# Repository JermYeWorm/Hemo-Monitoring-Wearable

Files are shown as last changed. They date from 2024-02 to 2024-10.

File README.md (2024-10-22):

# Hemodynamic Health Monitoring Wearable Platform
This device is an open-source, programmable, highly-integrated wearable platform capable of simultaneously measuring multiple hemodynamic biosignals. The goal is to enable real time processing by integrating both analog front end and edge ML, before wireless transmit. Our most recent paper can be found [here](https://doi.org/10.1109/MWSCAS60917.2024.10658959).
<br><br>
The current revision is electrical bioimpedance (EBI), electrocardiogram (ECG), and photoplethysmography (PPG) bio-monitoring enabled, and contains an onboard microprocessor and BLE transmit module.
<br><br>
The ongoing work on this project is with the Shah lab at the University of Maryland, College Park.
<br><br>

<br><br>

## System Flowchart

<br><br>

## Hardware
All PCB schematic capture and board layout was done with Altium Designer 2024.

The wearable platform runs on a BLE capable nRF52840 MCU SoC within a NINA-B302 FIFA antenna module. 
<br><br>
The MCU pinout is chosen to match the I2C, SPI, and spare analog/digital pins of an Arduino Nano 33 BLE. This allows for programmming via Arduino IDE after the burning of an Arduino Nano 33 BLE bootloader without the need for internal Arduino library pinout modifications. The MCU may also be programmed directly using the nRF Connect SDK.
<br><br>
The MCU is an open CPU and will require access through the SWD interface to enable programming through the USB port. A standard JLink with a 10 pin SWD cable connected to the J1 connector will allow for hardware debug and burning of bootloaders. 
<br><br>

<br>

<br><br>

### Schematic
Hierarchical Schematic Structure:<br>
```
├── [1] ipg_wearable.SchDoc
        ├── [2] sensors.SchDoc
        ├── [3] connectors.SchDoc
        └── [4] power_supply.SchDoc
```
<br>

1714973704757-3ba7de04-8b89-4758-92bf-7abcabce8b58_1
<br>

1714973704757-3ba7de04-8b89-4758-92bf-7abcabce8b58_2
<br>

1714973704757-3ba7de04-8b89-4758-92bf-7abcabce8b58_3
<br>

1714973704757-3ba7de04-8b89-4758-92bf-7abcabce8b58_4
<br><br>

### Board Layout

<br>_Fig 1. Top Layer (Signal)_<br><br>

<br>_Fig 2. GND Layer_<br><br>

<br>_Fig 3. PWR Layer_<br><br>

<br>_Fig 4. Bottom Layer (Signal)_<br><br>

<br>_Fig 5. Mechanical + Dimensions_<br><br>

### Fabricated Device

<br>_Fig 1. Front View_<br><br>


<br>_Fig 2. Back View (PPG Components Visible)_<br><br>

## Results

<br>_**(Top)** ECG with real time R-to-R detection using the onboard biopotential front end. **(Bottom)** EBI demonstration with electrodes placed across the thoracic cavity during respiration._<br><br>

## Contact
Inquiry about this repository can be directed towards jyun1129@umd.edu.

## Contributors
Primary Developer - Jeremy Yun (jyun1129@umd.edu)
<br>
Principal Investigator - Dr. Sahil Shah (sshah389@umd.edu)
<br>

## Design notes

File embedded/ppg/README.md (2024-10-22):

# PPG Front End Firmware

This directory contains jumpstarter resources for MAXM86146 firmware development. The MAXM86146 is pre-flashed with a programmable bootloader, and requires manual programming of an .msbl hex file via I2C to access application mode.
<br><br>
An .msbl flashing application can be found in "MAX32630FTHR_msbl_flasher" (requires external MAX32630FTHR board and 3.3V to 1.8V level shifter). 
<br><br>
"MAX32664C_33.13.31_MAXM86146.zip" contains the latest documentation from Maxim Integrated on the internal MAX32664C MCU.

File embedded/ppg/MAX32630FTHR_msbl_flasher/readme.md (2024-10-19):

# About
Software and firmware for flashing .msbl files using the [MAX32630FTHR](https://www.maximintegrated.com/en/products/microcontrollers/MAX32630FTHR.html).  This software flashes .msbl files onto a [MAX32664](https://www.maximintegrated.com/en/products/interface/signal-integrity/MAX32664.html) Biometric Sensor Hub.  The MAX32664 can be on one of Maxim's reference designs or on a custom PCB, provided that the necessary hardware connections are exposed correctly.
- RSTN
- MFIO
- SLAVE_SCL (external pull-up required)
- SLAVE_SDA (external pull-up required)
- VSS (GND)

Additionally, VDD power must be supplied to the MAX32664.  This can come from the MAX32630FTHR or from the target design.  This software uses 3.3V logic level.
It's recommended to power the MAX32664 from 3.3V for the flash, otherwise use a logic level translator to 1.8V.

# Usage
For a detailed usage guide, see:  [KA-13834](https://maximsupport.microsoftcrmportals.com/en-us/knowledgebase/article/KA-13834)

1.  Connect the SWD cable between the smaller MAX32625PICO programmer board ("pico") to the MAX32630FTHR ("fthr").

2.  Connect both boards to the host PC via the micro-usb ports.

3.  Drag and drop "MAX32630FTHR_msbl_flasher.bin" onto the DAPLINK drive to flash the "fthr" board.

4.  Remove the connections for the "pico" board.

5.  Connect the "fthr" board to the MAX32664.  For pin-outs on the "fthr" board, see [MAX32630FTHR Datasheet](https://datasheets.maximintegrated.com/en/ds/MAX32630FTHR.pdf)
	- Connect P3_5 to SLAVE_SCL (external pull-up required)
	- Connect P3_4 to SLAVE_SDA (external pull-up required)
	- Connect P5_6 to RSTN
	- Connect P5_4 to MFIO
	- Connect GND to VSS (GND) on the design
	- (Optional) Connect 3V3 to VDD, otherwise supply power from the MAX32664's board

6.  Open a command prompt and "cd" into this directory

7.  Run the command below to flash an msbl file.  Run flash.exe -h for help with the host program.

	`"flash.exe -f [msbl filename] -p [MAX32630FTHR COM Port]`

	Ex:  `"flash.exe -f "MAX32664C_OB07_WHRM_AEC_SCD_WSPO2_C_33.13.12.msbl" -p "COM16"`

	If the msbl file is not located next to the executable, you will need to pass in the full filepath.  
	Ex:  `-f "C:\Documents\MAX32664\msbl files\MAX32664C_OB07_WHRM_AEC_SCD_WSPO2_C_33.13.12.msbl"`

8.  Alternatively, the flashing program can be run as a Python (Python 3+) script.  "cd" into the Python directory and run "pip install -r requirements.txt".  Then, use...

	`"python flash.py -f [msbl filename] -p [your COM port]`
	
9. Alternatively, on Windows the included "run.bat" file can be used. This file will prompt the user to select from a list of .msbl files that were copied in the same location as the "flash.exe" file. Once the file has been selected by the assigned list number, then the console prompts the user to enter the assigned COM port to the MAX32630FTHR. Once this has been entered the program proceeds to flash the msbl file.

# Source Code
Full source code is available [here](https://github.com/MaximIntegratedTechSupport/MAX32630FTHR_msbl_flasher), and is dependent on mbed-os.  

The project can be built with mbed-cli, which is not straightforward to set up.  See https://maximsupport.microsoftcrmportals.com/en-us/knowledgebase/article/KA-15675.  With mbed-cli set up, run:

	mbed init
	mbed deploy (this will take a while)
	
and...
	
	mbed compile
	
... to build the firmware.

The flash.exe executable was generated from the Python source files with pyinstaller:
	
	pip install pyinstaller
	pip install auto-py-to-exe
	pyinstaller --noconfirm --onefile --console flash.py

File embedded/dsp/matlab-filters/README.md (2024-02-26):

# ECG Processing
This directory contains scripts for ECG signal conditioning. Main contents are various MATLAB scripts for power line coupling noise filtering and highpass baseline wandering filters.

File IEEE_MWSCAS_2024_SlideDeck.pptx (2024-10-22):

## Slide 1

Towards a Broadly Configurable Wearable Device
for Continuous Hemodynamic Monitoring

Jeremy Yun, Steeve Nzama, Sahil Shah

Department of Electrical & Computer Engineering
University of Maryland, College Park

2024 IEEE Midwest Symposium on Circuits and Systems
August 11th – 14th, Springfield, MA

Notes: Say name year school, say title, thank shah and steeve

## Outline

1. Introduction
2. Motivation
3. Comparison
4. System Architecture
5. Results
6. Conclusion & Future Work

## Introduction

- Cardiovascular diseases take ~20.5 million lives yearly
- Hemodynamically based signals are essential to early diagnostics
  - Most efficient method is through non-invasive, continuous monitoring, wearable devices
*Hemodynamic – blood related

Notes: Explain hemodynamic

Cardiovascular diseases is leading cause of death

Early diagnostics is critical, needs continuous monitoring

Talk about wearable devices

## Three Critical Biosignals

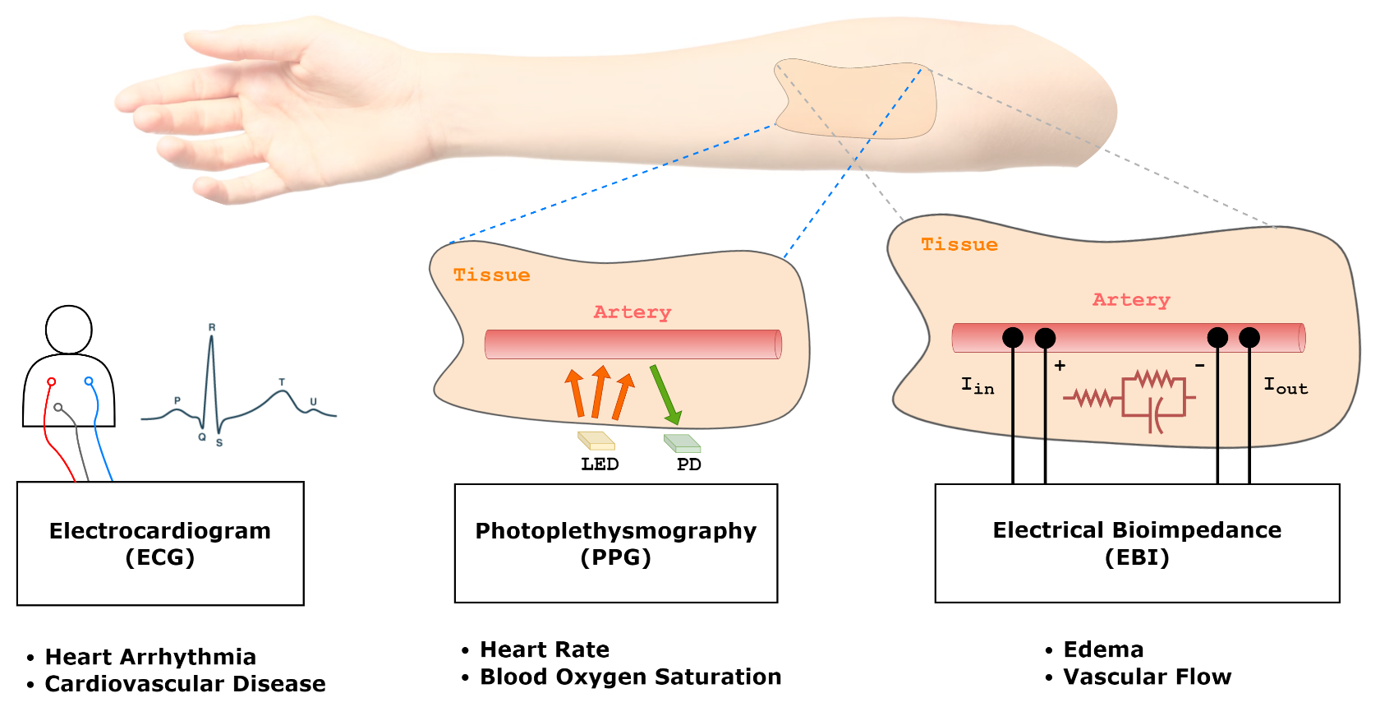
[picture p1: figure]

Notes: Within most cardiovascular diseases, these three biosignals can cover most applications

Explain how each signal is acquired

EBI less commonly found in wearable tech

## Improvement Opportunity for Wearables

Typical Wearables | Proposed Wearable
Measure a single biosignal Nonconfigurable | Multi-channel biosignal acquisition Broader hemodynamic monitoring applications
No onboard processing Only front end sensing | Onboard processing before wireless transmit Lower power Better data security Less latency
Proprietary Hardware | Open-source Hardware

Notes: Often nonconfigurable, unintegrated

Within academia, emphasis usually on front end sensing for a single application, less on backend integration

Commercial wearables have targeted applications, don’t have multiple channels.
Holter monitors dedicated to ECG, fitness wearables dedicated to PPG

Want to offer platform for full stack integration and new/broader multichannel applications

Lower power
Better data security
Less latency

## Concurrent Acquisition Examples

Pulse transit time (PTT) for blood pressure estimation
- Requires Δt between ECG R-peak & PPG rising edge

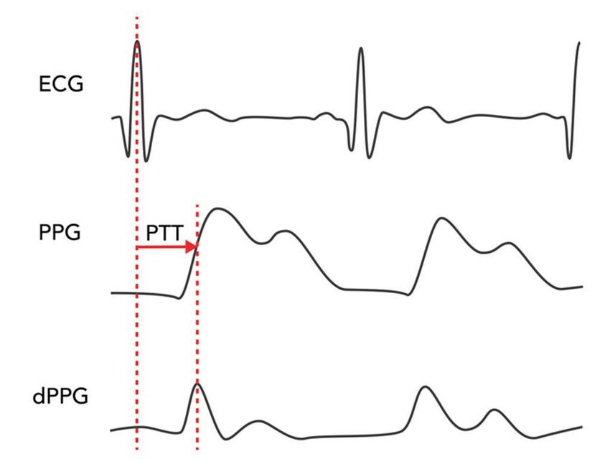
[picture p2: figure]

Impedance plethysmography (IPG) for blood flow monitoring
- Requires EBI and heart rate from ECG or PPG

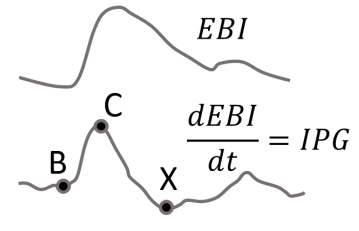
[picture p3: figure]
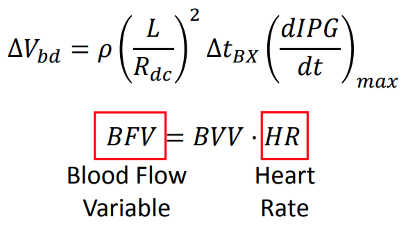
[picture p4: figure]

## Proposed System Flowchart

*mobile app is for visual illustration only

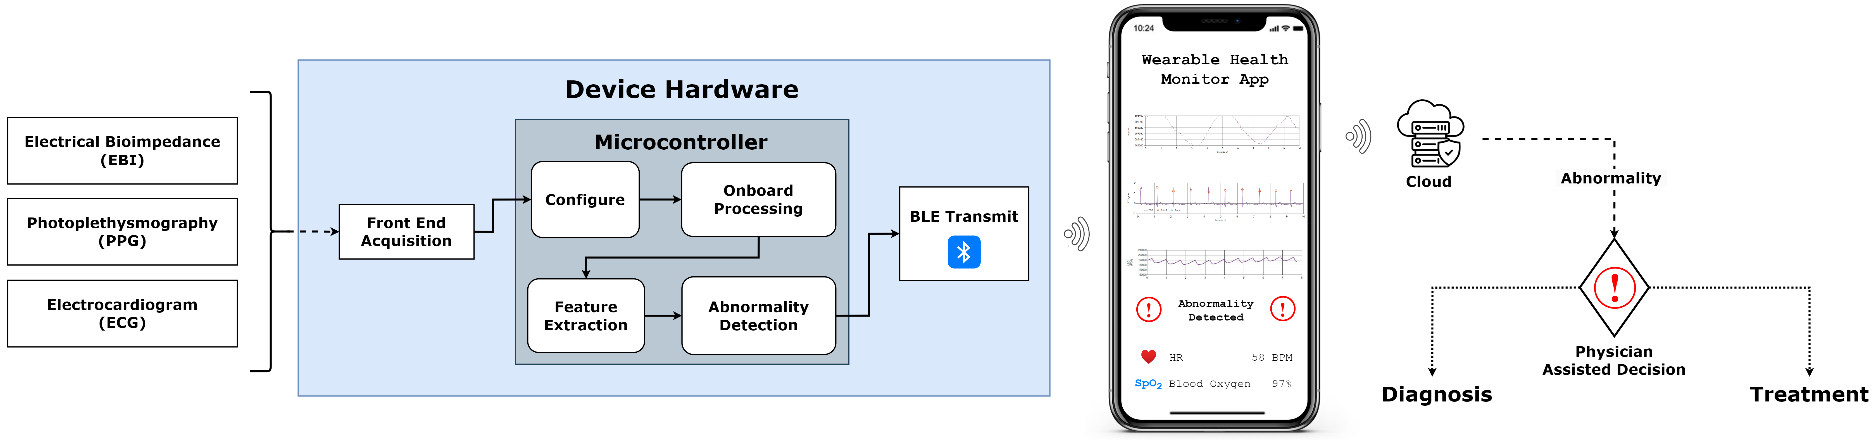
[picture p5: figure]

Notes: Focus is on the hardware

## Wearable Device Hardware

- 60.5mm by 38.75mm
- Integrated commercial ECG, EBI, PPG front ends
- Onboard microcontroller (MCU)
- Wireless transmit
- Power management system
- Open-source hardware

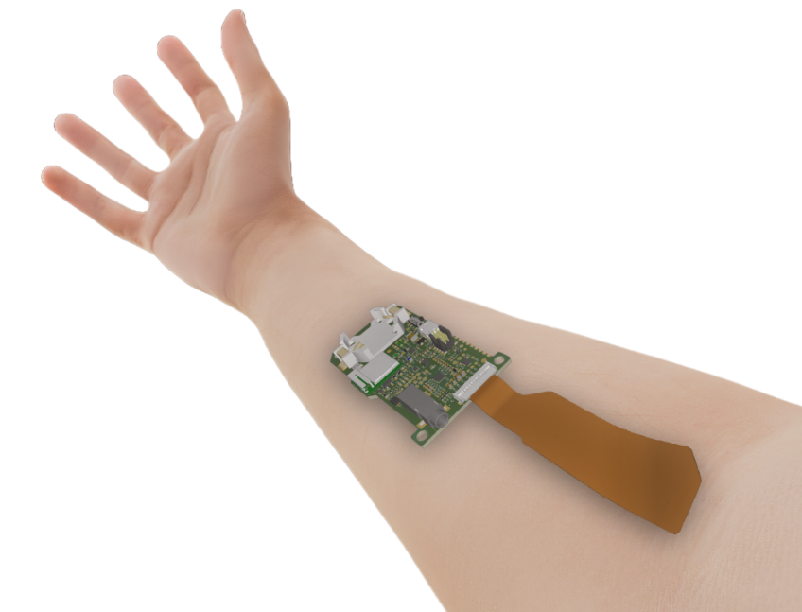
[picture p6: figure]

## Hardware Architecture

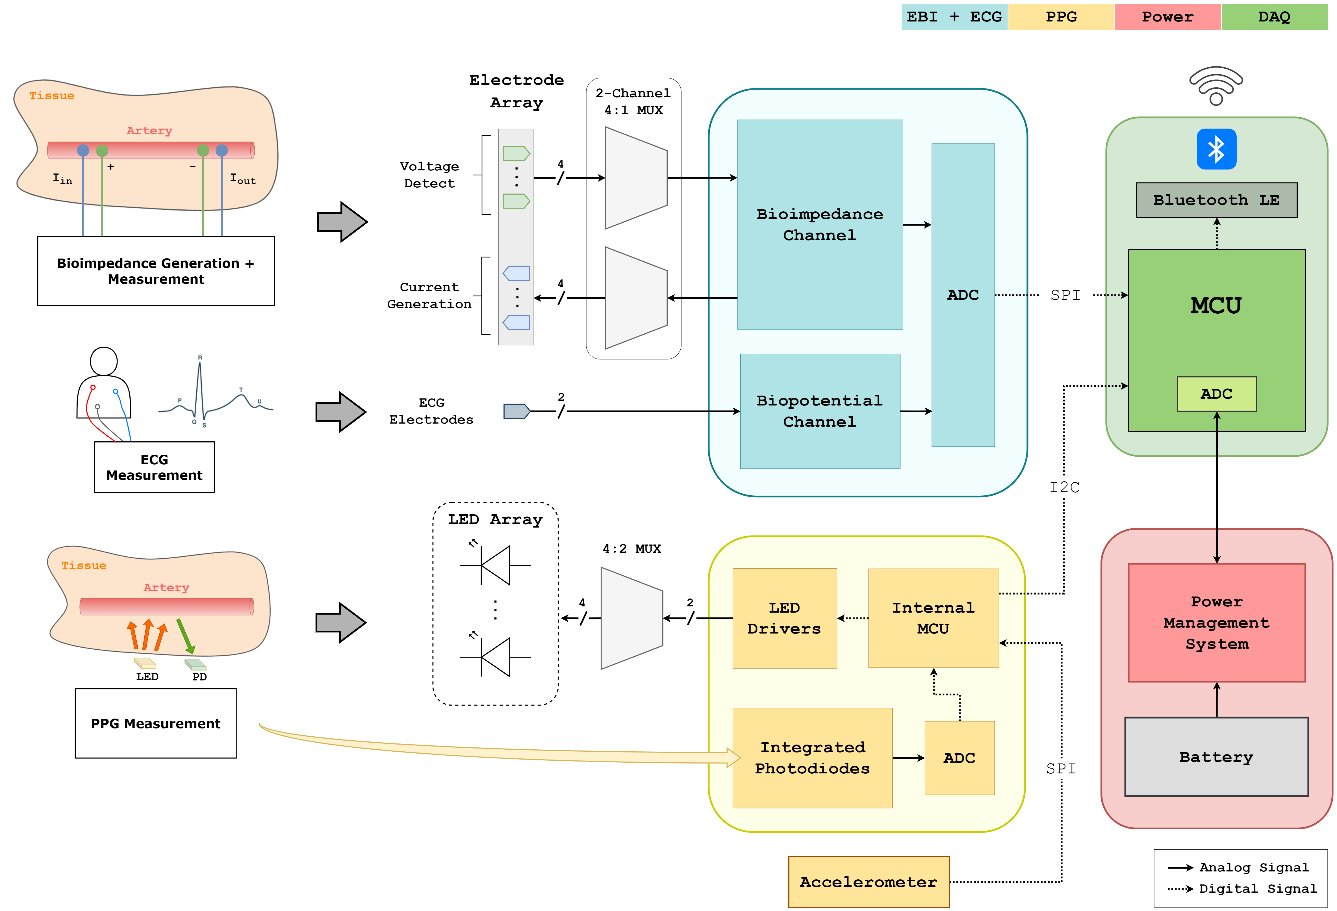
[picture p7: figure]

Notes: 4 main blocks color coded, on left are the front ends

## ECG & EBI Front End

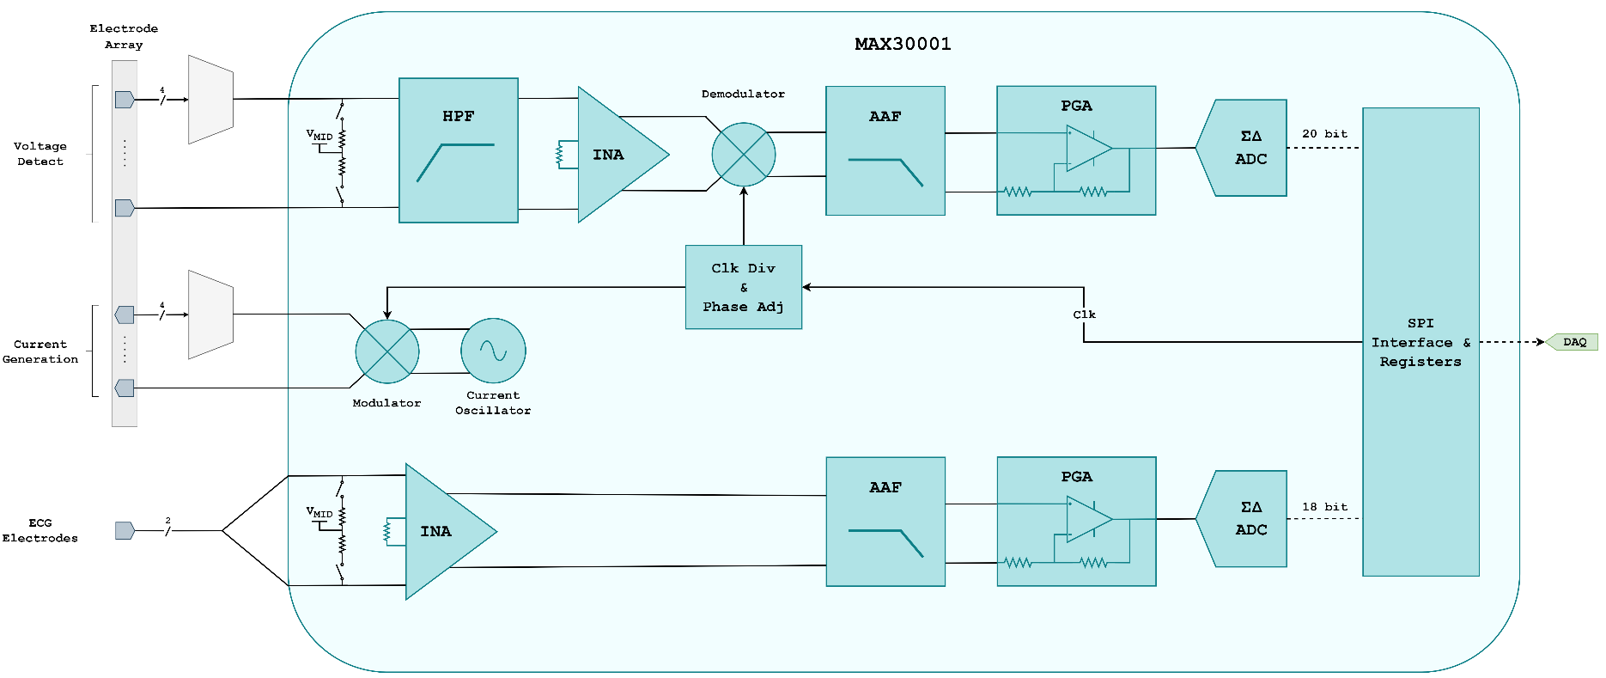
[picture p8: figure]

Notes: Generating current at configured levels and electrodes
Input is biased at a reference between your voltage rails to prevent saturation and eliminate common mode (no ref electrode needed)
In-amp takes the filtered voltage diff btwn electrodes
Gain can be programmed
Need phase sensitive circuitry to extract resistive and reactive


15.9 Bits ENOB (Effective Number of Bits) with 3.1µVP-P (typ) Noise for ECG
17 Bits ENOB with 1.1µVP-P Noise for BioZ

## PPG Front End

- Built around the MAXM86146 Optical Biosensing module
- Pulse heart rate and SpO2 modes
  - Multiwavelength LED array
- Integrated motion & ambient light compensation
- Peripheral 3-axis accelerometer

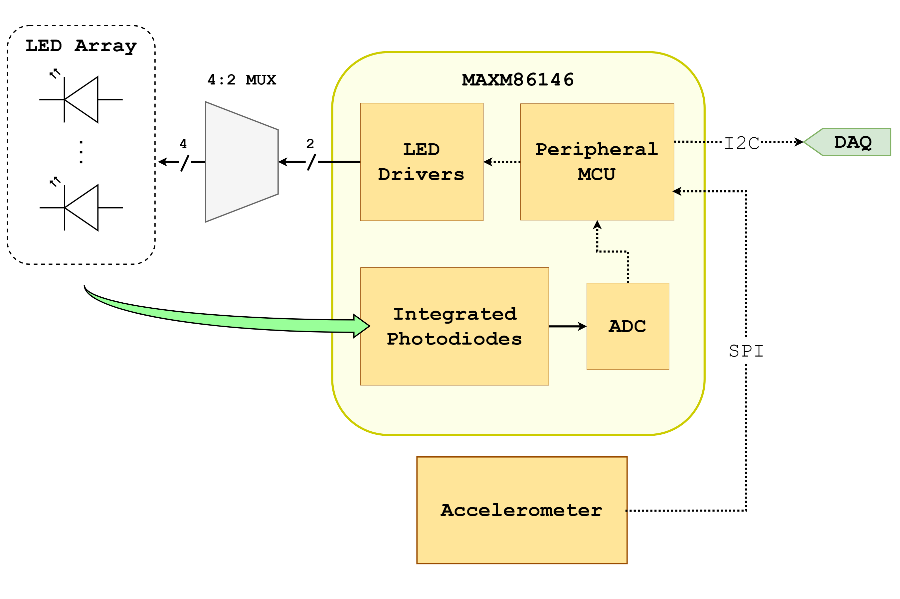
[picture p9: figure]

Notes: PPG system is built around commercial front end

At a high level, there are two modes, HR with green LEDs, SpO2 with red and IR
Hemoglobin has different spectra depending on its oxygenation

Compensation

## Data Acquisition Unit (DAQ)

- nRF52840 microcontroller (MCU) SoC
  - Bluetooth (BLE) capable
  - Extensive development resources
    - Arduino library compatible
    - Wearable & IoT heritage
- Processes input from front ends
  - Feature extraction
- Performs battery monitoring

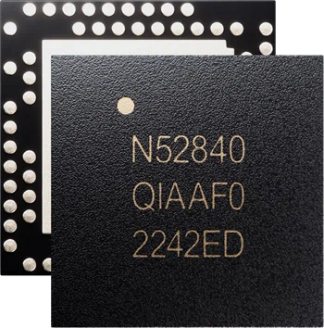
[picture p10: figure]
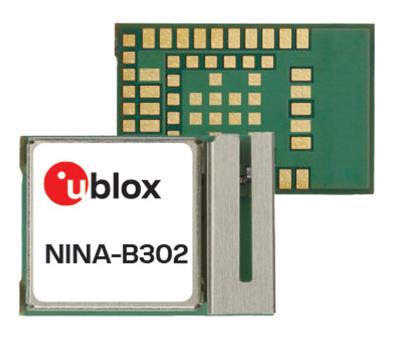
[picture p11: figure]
NINA-B302

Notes: ARM M4 Cortex CPU
Internal ADC & memory

## Power Management System

- Battery either:
  - CR2032 coin cell battery
  - LIR2032 rechargeable coin cell
- Monitoring requires only a few seconds of measurement every few hours
  - 2 min/day
    - CR2032 last over 2.5 months*
    - LIR2032 need recharge every 2 weeks*
*Calculated from datasheets

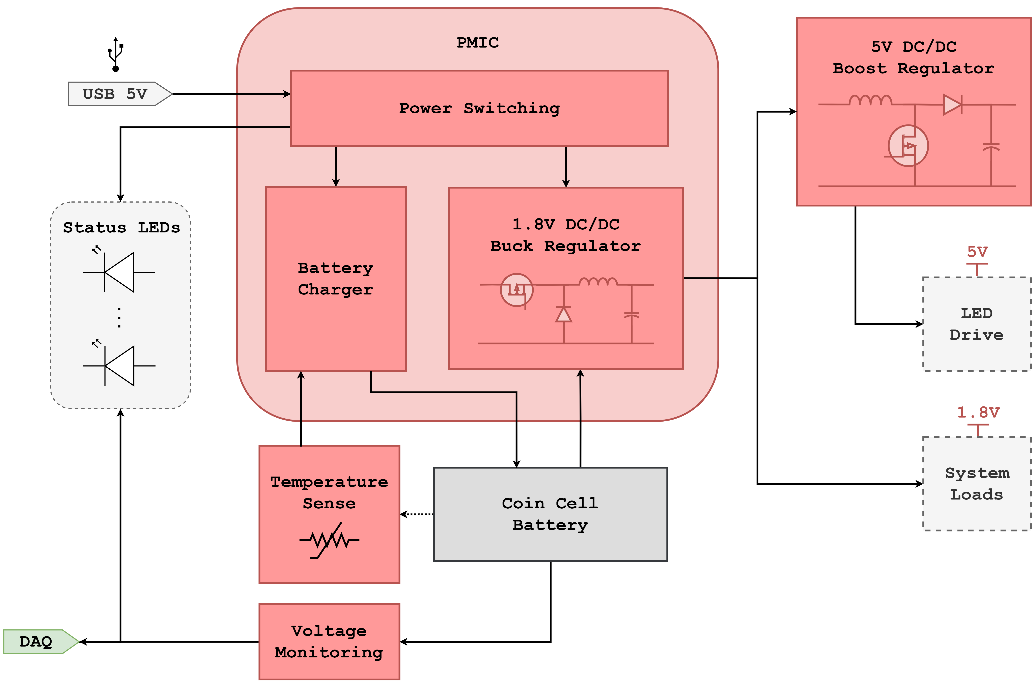
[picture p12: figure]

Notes: Power management is very important for continuous monitoring wearables

With all systems active and transmitting, a CR2032 battery is depleted in a day

PPG Is by far the most power intensive (LED drive current) – 90% of power draw
Only ECG and EBI would last over a year

## Device Physical Model

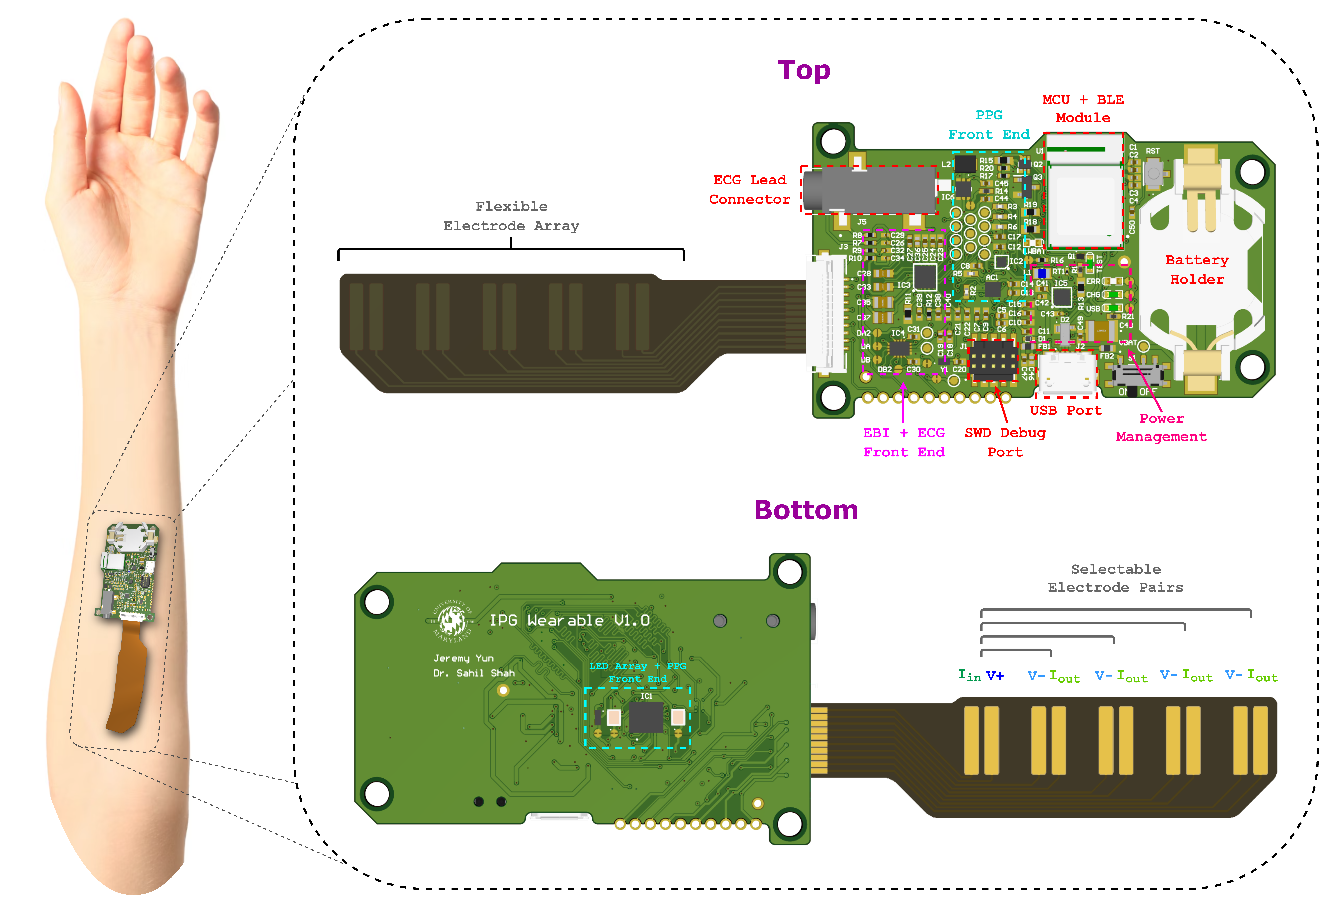
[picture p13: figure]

*electrode array may be
customized to other shapes

## Results

- ECG signal from the analog front end
  - Real time R-to-R detection
  - Onboard signal filtering & noise removal

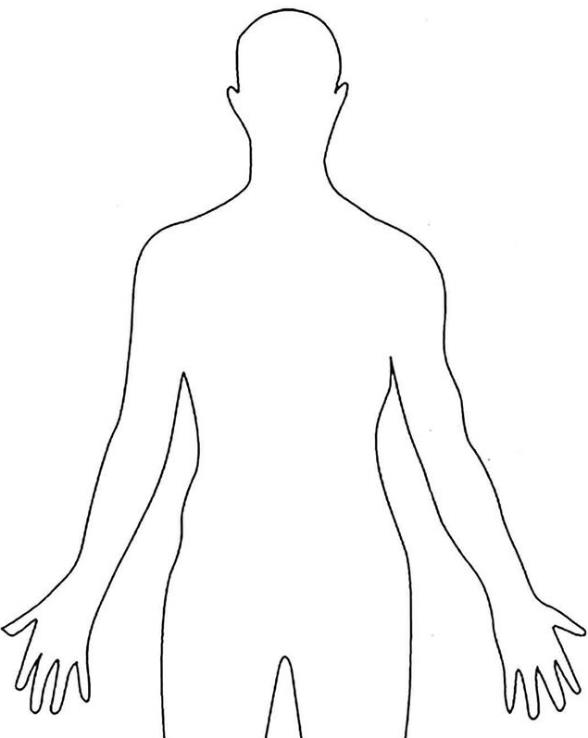
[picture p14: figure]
Human Body Template | room surf.com

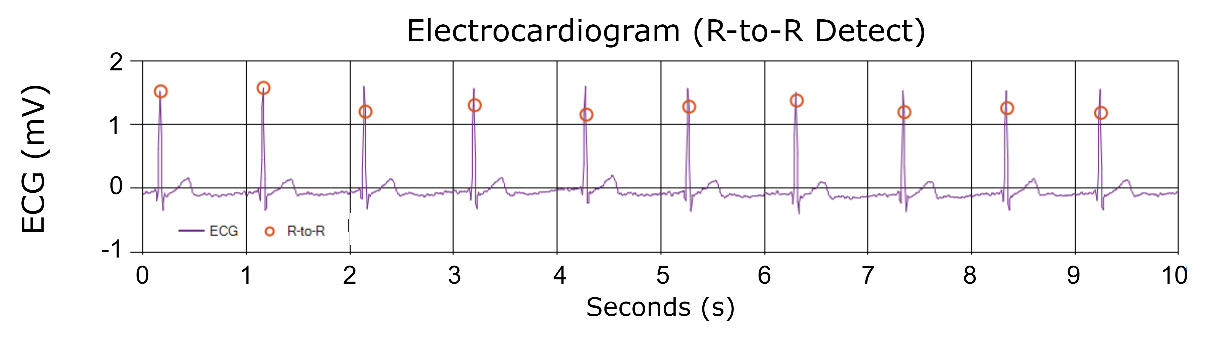
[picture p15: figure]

+

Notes: Healthy patient

Concurrently measured with…

## Results

- EBI signal from the analog front end
  - Electrodes placed across thoracic cavity during respiration
  - Current injection configured to 8μA amplitude at 16kHz
    - Within IEC-60601 standard

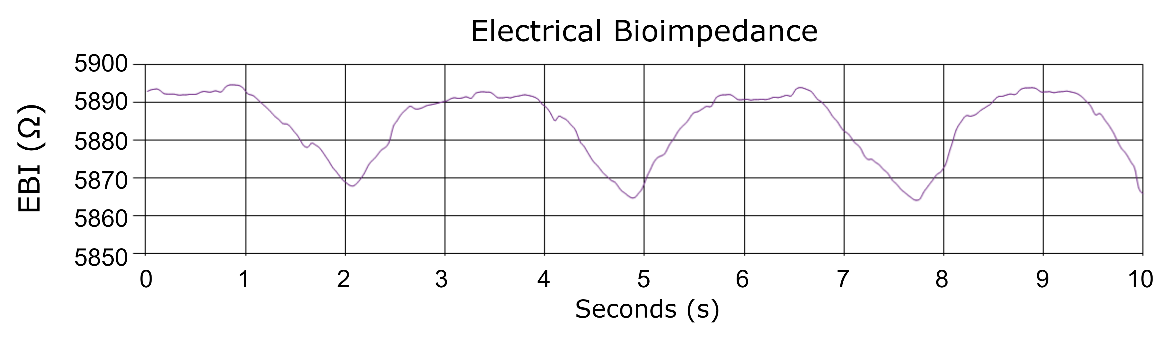
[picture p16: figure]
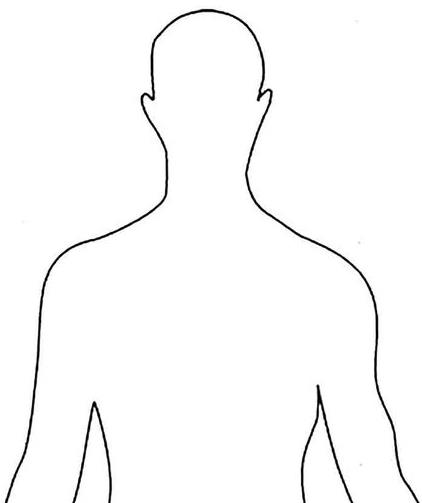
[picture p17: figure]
Human Body Template | room surf.com
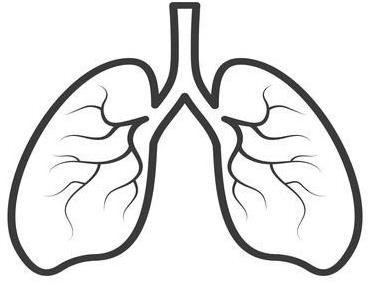
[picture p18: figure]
Human Lungs Icon Vector Illustration Graphic by juliochaniago55 · Creative Fabrica

IN

+

OUT

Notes: Freq in the kHz range to penetrate thoracic cavity
Current level chosen to remain within the IEC-60601 standard perception threshold

## Comparison Table

| [1] | [2] | [3] | [4] | Proposed Device
Sensor Type | ECG, EBI, PPG | EBI | ECG, EBI | ECG, EBI, PPG | ECG, EBI, PPG
EBI Resolution [mΩ] | 200 | 100 | N/A | 66 | 40
Size [mm²] | 130 x 70 x 20 | Nonintegrated | 50 x 90 x 15 | 29 x 90 x 20 | 60 x 39 x 15
Current Draw [mA] | 23.6 | 50 | 440 | 25 | 0.221*
Open-Source HW? | No | No | No | No | Yes

*Not including LED drive (will depend on application)

[1] G. Squillace et al., "Bio-impedance System for Wearable Vital Sign Monitoring", 16th International Conference on Electrical Bio-Impedance (ICEBI), pp. 60, 2016.
[2] S. Hersek et al., “A Robust System for Longitudinal Knee Joint Edema and Blood Flow Assessment Based on Vector Bioimpedance Measurements,” IEEE Transactions on Biomedical Circuits and Systems, vol. 10, no. 3, pp. 545–555, Jun. 2016, IEEE Transactions on Biomedical Circuits and Systems
[3] J. Ferreira et al., "Portable bioimpedance monitor evaluation for continuous impedance measurements. Towards wearable Plethysmography Applications", Proceeding of the 35th Annual International Conference of the IEEE Engineering in Medicine and Biology Society, pp. 559-562, 2013.
[4] S. Lee, B. Grundlehner, R. G. van der Westen, S. Polito and C. Van Hoof, "Nightingale V2: Low-power Compact-sized Multi-Sensor Platform for Wearable Health Monitoring," 2019 41st Annual International Conference of the IEEE Engineering in Medicine and Biology Society (EMBC), Berlin, Germany, 2019, pp. 1290-1293, doi: 10.1109/EMBC.2019.8856847.

## Conclusions & Future Work

- Proof-of-concept signal acquisition demonstrated
- Configurable open-HW platform can aid in rapid algorithm development
- Future steps:
  - More channels (e.g. ultrasound)
  - Use as a platform to target specific conditions

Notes: Add more acquisition capability to enable HW to be used for broader range of applications

Following this, can using this as a platform to hone-in on more specific applications

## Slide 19

Thank You!
Questions?
Contact: jyun1129@umd.edu

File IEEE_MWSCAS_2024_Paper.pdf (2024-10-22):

# Towards a Broadly Configurable Wearable Device for Continuous Hemodynamic Monitoring

Jeremy Yun, Steeve Nzama and Sahil Shah Department of Electrical and Computer Engineering University of Maryland, College Park, MD, USA. E-mail: jyun1129@umd.edu, sshah389@umd.edu.

Abstract—Hemodynamic signals, such as Electrocardiogram (ECG), Photoplethysmography (PPG), and Electrical Bioimpedance (EBI), provide a myriad of critical health indicators. For instance, ECG is utilized by cardiologists to diagnose a range of cardiovascular diseases, PPG estimates blood oxygen levels, and EBI gauges vascular flow. A multimodal device capable of continuously monitoring these signals can furnish healthcare professionals with profound insights into patient well-being. This paper introduces a hardware design for a programmable, wearable device that measures multiple physiological signals, including ECG, PPG, and EBI. Equipped with an onboard microprocessor, the device enables real-time data processing. Compact and efficient, the system measures just 60.5mm by 38.75mm, has low-power dissipation, and is powered by a coin cell battery. Using largely discrete commercial components and a custom electrode array, the open-source hardware allows for rapid configurability and broad usage applications within the health monitoring domain.

I. INTRODUCTION
Cardiovascular disease is the leading cause of death globally, with an estimated 20.5 million lives being taken each year [1]. Heart and vascular disorders affect approximately 121.5 million adults, or 48% of individuals in the United States alone [2]. Hemodynamically based signals such as Electrocardiogram (ECG), Photoplethysmography (PPG), and Electrical Bioimpedance (EBI) offer critical health indicators essential to modern medical diagnostics for these diseases. ECG serves as a non-invasive tool for cardiologists to diagnose various heart diseases by capturing the heart’s electrical activity and identifying abnormal patterns. PPG measures blood oxygen levels, providing vital data on pulmonary function and circulatory health, while EBI provides insights into body composition and fluid distribution, crucial for monitoring vascular flow [3]. Non-invasive monitoring of vascular flow can offer indispensable information for assessing the health of vascular and tissue systems without the need for intervention or surgery [4]. Collectively, these technologies enable a comprehensive evaluation of a patient’s health, facilitating the early detection and management of medical conditions.
A variety of commercial and academic devices are available that support the measurement of ECG and PPG [5], [6]. Portable devices that measure EBI have also been developed, enhancing the assessment of vascular flow and body composition. Notably, devices described in Hersek’s 2017 study highlight the utility of EBI in wearable technology, providing deeper understanding of fluid dynamics and tissue

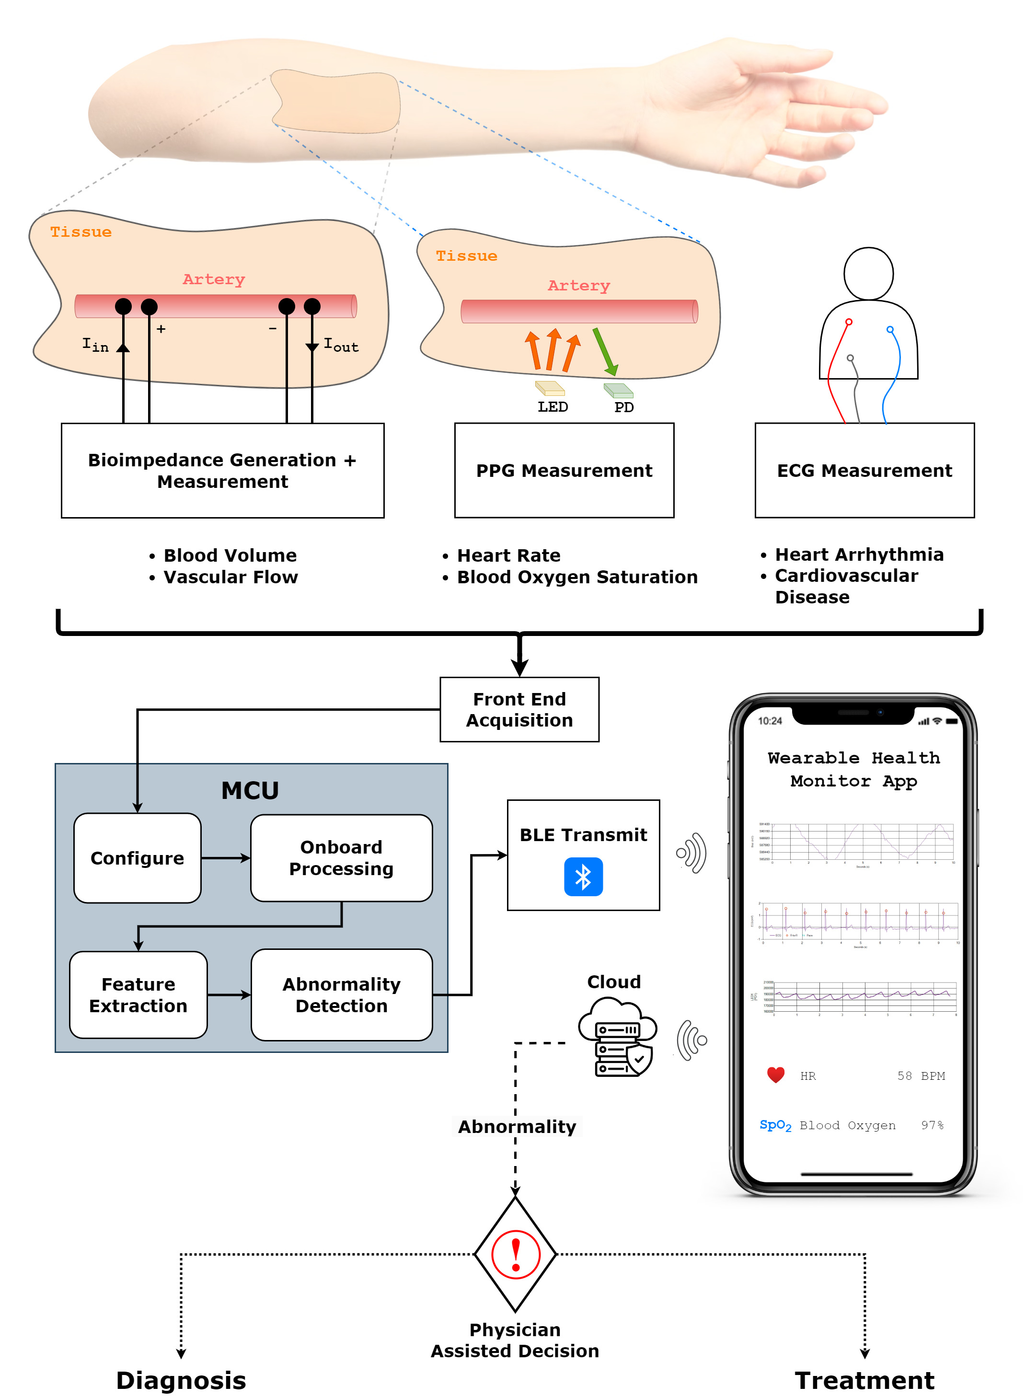
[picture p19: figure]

Fig. 1: Overall system flowchart displaying real-time onboard processing and configurability of the device for multiple biosignals.

properties [7], [8]. Such devices are instrumental in the prompt detection of physiological abnormalities, enabling clinicians to more accurately diagnose problems and recommend suitable treatments.
Typically, wearable device designs focus on specific hardware systems tailored to measure distinct physiological signals. Commercially available PPG devices, for example, are engineered specifically to assess blood oxygen levels [6]. Devices dedicated to ECG recordings primarily monitor cardiac activity [5]. However, comprehensive patient health assessment often necessitates the simultaneous measurement of multiple physiological signals.

Furthermore, previous designs of hemodynamic measuring devices often feature large, discrete, front-end-only platforms rarely integrated onto a single device. Few possess both onboard processing and wireless transmit capabilities. For example, the cuff-less blood pressure monitoring wearable introduced in Rachim and Chung’s 2019 study includes a small wrist worn EBI and PPG front end sensor with integrated electrodes [9]. However, only the analog front end (AFE) is integrated on the wearable; data acquisition and processing units remain offboard. Similarly, the device in Hersek’s 2017 study presents a wearable EBI AFE with an onboard MCU and discrete electrodes, but important post-processing tasks such as feature extraction are performed offboard without wireless transmit [7]. Even fewer systems include the various channels of biosignal sensing capacity needed for broader hemodynamic monitoring.
To address this need, by utilizing readily available discrete commercial bio-aquisition front ends, this work aims to describe a smaller yet more comprehensive, more power efficient yet similarly capable platform more suitable for wearable applications. An open-source, programmable, highly-integrated wearable platform capable of simultaneously measuring ECG, PPG, and EBI is thereby presented. This device also features an onboard microprocessor that supports real-time processing of physiological signals, significantly enhancing its capability for continuous health monitoring. Figure 1 depicts the overall system architecture.

II. BIOSIGNAL MEASUREMENT

A. Electrocardiogram
The electrocardiogram is the most commonly used noninvasive technique for gleaning information about the cardiac muscle contraction sequence and nominal heart functioning. Physiological markers which can be monitored through an ECG’s QRS complex include R-to-R heart rate, arrhythmia, pacemaker malfunction, cardiomyopathy, rheumatic heart disease, along with symptoms associated with cardiac diseases such as tachycardia and bradycardia, among others [10]. The measurement of ECG signals in a clinical setting typically involves a standard 12-lead setup [11]. However, for most wearable ECG applications, a 3-lead or single-lead setup is sufficient for basic diagnostic purposes [12]. At its core, an ECG measures the potential difference between sets of two points on the skin, otherwise known as leads, as electrical impulses from the heart traverse through the body. In its simplest form, this is achieved using two conductive electrode pads interfacing the skin, which are fed through as inputs to an instrumentation amplifier [13]. The instrumentation amplifier is composed of a difference amplifier with two input buffer amplifiers, negating the need for impedance matching and providing gain adjustability through a single resistor.
Raw ECG measurements are inherently noisy signals, and external artifacts such as baseline drift, 50/60 Hz power line coupling, electrode contact quality, respiration, and motion artifacts must be accounted for [14]. Signal noise can be mediated with both analog and digital bandpass filters. To ensure that the common-mode voltage of the leads avoid amplifier saturation, the patient’s body must be voltage driven to a level such that the electrodes are DC biased to within the input range. This is commonly performed using a right-leg drive (RLD) circuit, requiring an additional “ground” reference electrode. However, 2-electrode systems offer greater hardware efficiency, and can be achieved by biasing the input electrodes to within the voltage range of the acquisition system’s data converter [15]. Portable and wearable ECGs have gained in prevalence. However, accurate ECG signals must still be measured across the heart, limiting the local measurement ability of limb-worn wearables, thereby constraining many long-term monitoring use cases.
B. Photoplethysmography
Found in many health wearables, photoplethysmography offers a more compact, more localized, but less power efficient sensing solution in comparison to ECG for certain cardiac monitoring applications. In principle, PPG operates by illuminating skin tissue with specific wavelengths of light emitted from an LED. Light absorbed, reflected, or transmitted through the skin is then measured with a photodiode sensor and converted to an electrical signal, which can vary as a subcutaneous organ changes in volume. With each cardiac cycle, pressure waves sent through the cardiovascular system cause blood vessels to dilate, which can be measured via PPG. A large limitation to PPG systems are their susceptibility to motion and external light artifacts. Additional 3-axis calibration accelerometers and ambient-light cancelling algorithms are therefore necessities when such systems are used in wearables [6].
Much like ECG, the periodicity of the PPG signal can be used to determine heart rate. For heart rate monitoring, green (∼530 nm) LEDs are typically used. For blood oxygen saturation monitoring (SpO2), red (∼660 nm) and infrared (∼940 nm) LEDs are typically used [16]. PPG is often used in conjunction with other biosignals such as ECG and EBI. For example, to calculate pulse transit time (PTT) for systolic blood pressure (SBP) estimation, a key marker for hypertension, the time difference between the R-peak of an ECG signal and the systolic peak of a concurrently measured PPG signal must be calculated, highlighting the importance of parallel multi-biosignal measurement [17].
C. Electrical Bioimpedance
Electrical bioimpedance measurements provide another host of biomonitoring applications, namely blood volume measurements and vascular flow. For impedance plethysmography (IPG) utilizations, injected AC current from an oscillator is passed through an area of skin containing a target artery via an electrode pair. As blood flow volume pulses, the impedance of subsurface tissue is altered. These pulses are measured using an additional set of voltage detect electrodes measuring the change in potential difference across the area of skin. Similarly to ECG, this voltage is measured using an instrumentation amplifier setup. Due to the nature of skin presenting a high complex impedance against low frequency current, high frequency low magnitude sinusoidal AC current must be used [18]. Typically, IPG injection current frequencies lie between 10kHz to 100kHz for sufficient tissue penetration [19]. Current magnitudes usually remain under the perception threshold Imax = 10⁻⁷ ∗ freq to maintain user safety under the IEC-60601 standard [20]. EBI acquisition hardware must also leverage phase-sensitive detection to extract both resistive and reactive components of skin impedance.
Following acquisition, the measured EBI waveform is used to construct the IPG signal using (1).

IP G =

dEBI
dt | (1)

Subsequently, pulsatile blood volume (∆Vbd) can be found using (2), where ρ is blood resistivity, L is the distance between voltage electrodes, Rdc is the DC resistance of tissue, ∆tpulse is the time difference between the minima preceding and following each EBI pulse, and

dEBI
dt |
| max is the rising
edge amplitude of the IPG signal.

∆Vbd = ρ

L

Rdc 2
∆tpulse
dEBI

dt

max

(2)

Finally, the blood flow rate (Qbd) is calculated using (3), where HR corresponds to heart rate.

Qbd = ∆Vbd · HR | (3)

As such, to calculate blood flow rate, EBI must be measured concurrently with either the systolic peaks from PPG or R-to-R detection from ECG [21].

III. HARDWARE ARCHITECTURE
The wearable device hardware consists of several tightly integrated biosignal front ends capable of monitoring ECG, EBI, and PPG signals, in addition to an onboard MCU with wireless transmit capabilities and a tailored power management system. The platform measures 60.5mm by 38.75mm at its widest and is implemented on a 4-layer PCB. The overall hardware block diagram presented in Figure 2 visualizes the EBI + ECG and PPG front ends, power, and data acquisition (DAQ) module blocks. A labelled view of the custom fabricated electrodes and device is displayed in Figure 3. The system’s hardware design files are open-sourced and available to the public.
A. ECG & EBI Front End
The EBI front end interfaces with the patient’s skin using a custom flexible dry electrode array. The electrode array can be printed on a flexible substrate, or fabricated as a flex PCB where the electrode pads are coated with Ag/AgCl. The onboard ribbon connector enables tailor designed electrodes for maximum adaptability regardless of device placement on the body. To collect data across varying lengths and current penetration depths of tissue, the default wearable device utilizes an array of four sets of current generation and voltage detect electrodes. The electrode pairs are spaced apart by distances from 1cm to 4cm in 1cm increments. The pairs can be selected using a 2-channel 4:1 multiplexer (MUX).

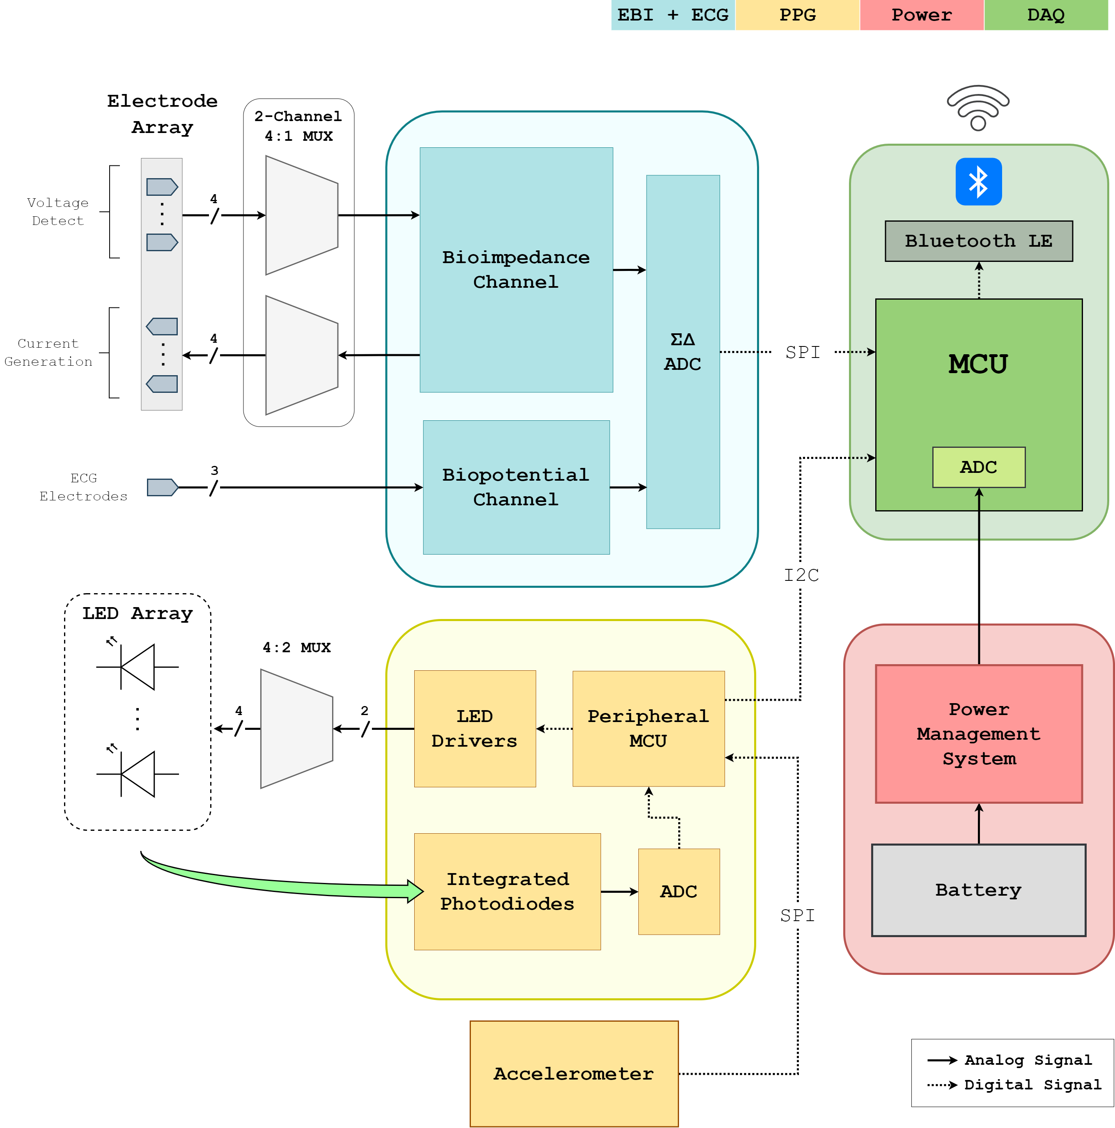
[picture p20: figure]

Fig. 2: Block diagram of the hardware.

The ECG front end input is accessed through a 3.5mm barrel connector jack using a set of commercial 3-lead ECG electrodes, with the third reference electrode optional. To obtain a clear signal, the positive and negative leads must cover sufficient body surface area such that the ECG signal vector can provide sufficient potential difference to be detected. The acquired ECG and EBI signals are passed through passive low pass filters before being acquired by a MAX30001 Ultra-Low-Power Integrated Biopotential and Bioimpedance AFE (Analog Devices, Inc, Norwood, MA). Both the ECG and EBI channels have their own respective 18-bit and 20-bit Σ∆ analog-to-digital converters (ADC’s). The MAX30001 is supplied with a constant 1.8V VDD level.
For both ECG and EBI signal acquisition, internal DC lead biasing drives the connected tissue to an appropriate common mode voltage level when using a single lead (two electrode) setup. The common-mode voltage of the positive and negative electrodes is body biased to an average DC level (VM ID), which can be calculated as VM ID =

VDD
2.15 = 837mV . The
input electrode voltage range can subsequently be bandlimited to VM ID ± 550mV maintaining within the saturation requirements of the MAX30001’s VDD. For EBI signal acquisition, the magnitude and frequency of the injection current is selectable to be between 8µA to 96µA and 125Hz to 128kHz, respectively.
B. PPG Front End

The system also contains a complete photoplethysmography system capable of monitoring both pulse heart rate (HR) and pulse blood oxygen saturation (SpO2). The PPG system contains an LED array consisting of two green (536 nm) LEDs, a red (655 nm) LED, and an infrared (940 nm) LED.

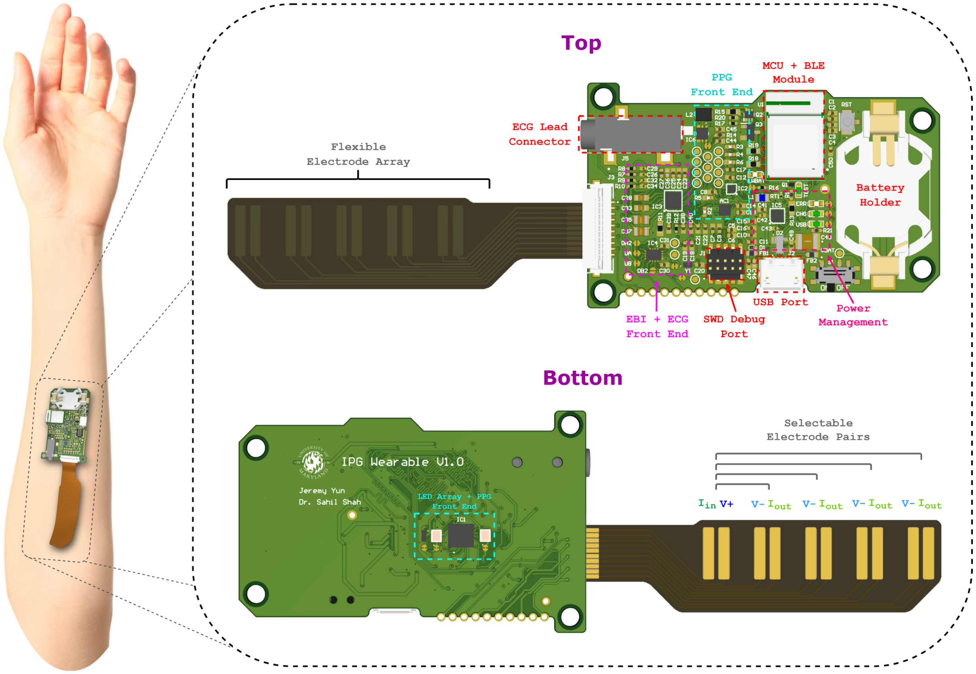
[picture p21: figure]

Fig. 3: Custom printed circuit board and flexible electrodes used for measuring the physiological signals.

The assorted wavelengths allow for both heart rate (dual green LEDs) and SpO2 (Red and IR LEDs) configurations, which can be toggled with a peripheral 4:2 MUX. The reflected PPG light is sensed by two photodiodes integrated on a MAXM86146 Optical Biosensing Module with an internal processor (Analog Devices, Inc, Norwood, MA). A peripheral accelerometer communicates with the MAXM86146 via Serial Peripheral Interface (SPI), enabling motion artifacts to be removed with embedded algorithms in the internal processor. The PPG front end has internal LED drivers with configurable PWM and LED supply current, along with built in ambient light cancellation.

C. Data Acquisition Processing Unit
The device’s primary microcontroller unit (MCU) contains an nRF52840 Multiprotocol Bluetooth 5.4 System-on-Chip (SoC) (Nordic Semiconductor ASA, Trondheim, Norway). The MCU is built around a 32-bit ARM M4 Cortex CPU with floating point unit running at 64 MHz and an internal ADC. The MCU also holds 1 MB of internal flash memory and 256 kB of RAM. The nRF SoC is encapsulated within a NINA-B302 Bluetooth Low Energy (BLE) module with an onboard PIFA antenna (u-blox, Thalwil, Switzerland). The primary MCU receives data from the MAX30001 EBI and ECG front end via SPI and the PPG data from the MAXM86146 via the I2C protocol. The MCU pinout configuration is designed for compatibility with an Arduino Nano 33 BLE bootloader and library in an unmodified state to allow for easy embedded software bring-up.
D. Power Management System
All onboard device components run on an energy efficient 1.8V with the exception of the LEDs, which require a 5V step-up boost converter. A highly power efficient battery management system with charging capability allows for long-term continuous usage of the device without battery replacement or frequent charging. The power management system contains an nPM1100 power management IC (PMIC) with an integrated DC/DC Buck regulator configured to 1.8V (Nordic Semiconductor ASA, Trondheim, Norway). The device may be powered either by a 3V single-use CR2032 coin cell battery or a 3.7V LIR2032 rechargeable coin cell. The PMIC contains Li-ion battery charging internals set to a 35mA charge current limit for LIR2032 battery compatibility. The device is rechargeable via Micro-USB if an LIR2032 is used. Custom battery monitoring and temperature tracking circuitry with discrete components are also included. Sampled battery voltage data is processed using the MCU for low battery indication. With all device systems continuously active, including PPG LEDs, the device would consume a maximum load current of ∼125mA, depleting a CR2032 battery in 2 hours. However, in most scenarios a few seconds of measurement every few hours is sufficient for continuous monitoring purposes, in which case a typical CR2032 would last over 2 ¹
2 months, and an LIR2032
would require recharge only every 2 weeks.

IV. RESULTS & DISCUSSION
The platform’s biosignal channel modules were individually tested using commercially provided evaluation boards provided by the biosignal front end vendors. For the ECG and EBI data acquisition, a MAX30001EVSYS evaluation platform (Analog Devices, Inc, Norwood, MA) was used to test the MAX30001. Figure 4 illustrates the real-time concurrent acquisition of an ECG and EBI signal collected from a healthy subject. The ECG signal was acquired using a single lead setup with electrodes placed on both forearms. Active

R-to-R detection is demonstrated on the output waveform displayed via a connected GUI. For the EBI demonstration, current with a 16kHz excitation frequency and 8 µA magnitude was injected across the subject’s chest and recorded normal respiratory behavior using voltage detect electrode pairs. As the subject inhaled, internal volume of the thoracic cavity increased; during exhale, the volume decreased, registering corresponding changes in measured EBI. As shown in Figure 4, the resulting waveform reflects the captured respiratory cycles. For both cases, all signal filtering, conditioning, and artifact removal was performed onboard the front end.

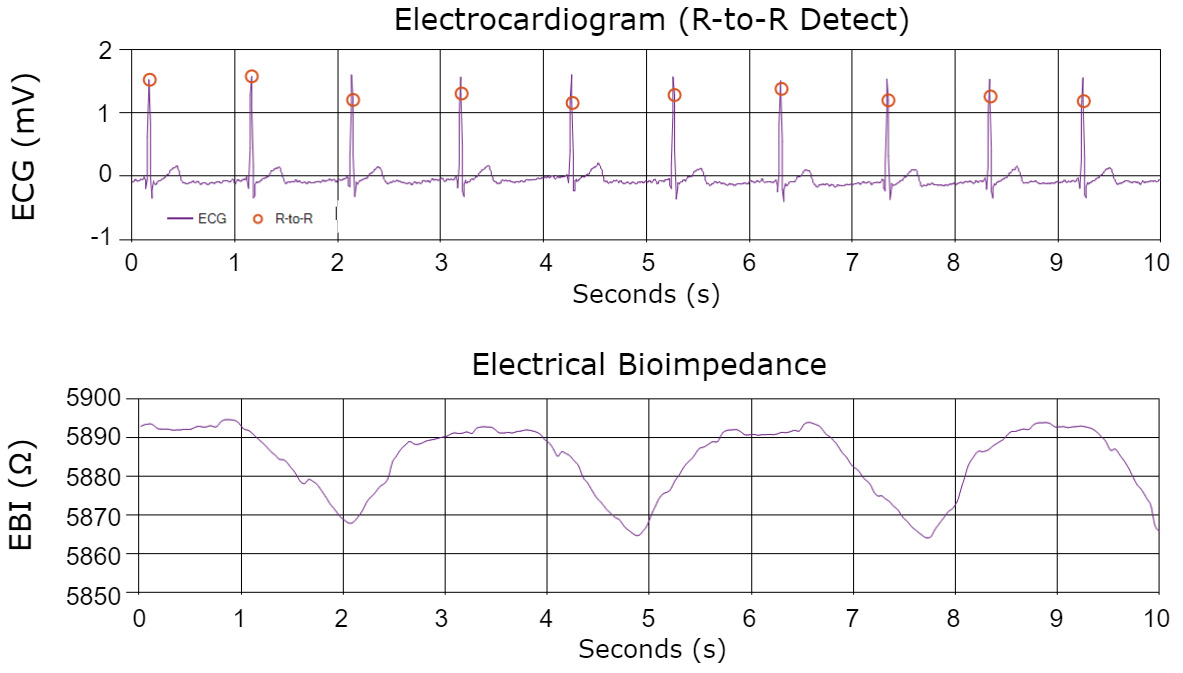
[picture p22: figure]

Fig. 4: (Top) ECG with real time R-to-R detection using the onboard biopotential front end. (Bottom) EBI demonstration with electrodes placed across the thoracic cavity during respiration.

V. CONCLUSION & FUTURE WORK
In this paper, a compact, low-power, open-source, and configurable continuous health monitoring wearable is presented. The platform contains multiple biosignal channels, including ECG, PPG, and EBI, and is capable of onboard processing and wireless transmit. Proof-of-concept efficacy of the acquisition channels are also demonstrated. To our knowledge, such an integrated platform has thus far not been explored in the literature. We envision that this open-hardware platform can be referenced to aid future rapid prototyping of wearable monitors for similar applications. Future steps include further miniaturization, the design of a mechanical packaging, and fabrication on a flexible substrate. Additional directions include the addition of ultrasound-based sensing capabilities and deeper investigations into implementing software algorithms for monitoring specific health applications, such as arteriovenous fistula (AVF) IPG monitoring.

VI. CODE
The GitHub repository containing the hardware design files and documentation can be found at: https://github.com/JermYeWorm/Hemodynamic-Monitoring-Wearable. (https://github.com/JermYeWorm/Hemodynamic-Monitoring-Wearable)

VII. ACKNOWLEDGEMENT
We would like to acknowledge partial support of National Science Foundation via award number 2322699 through the experiential learning program. The award enabled Steeve Nzama to perform research at University of Maryland, College Park.

REFERENCES

[1] M. Di Cesare et al., “The Heart of the World,” Global Heart, vol. 19, no. 1, p. 11, Jan. 2024.
[2] S. S. Martin et al., “2024 Heart Disease and Stroke Statistics: A Report of US and Global Data From the American Heart Association,” Circulation, vol. 149, no. 8, pp. e347–e913, Feb. 2024, publisher: American Heart Association.
[3] S. Hersek et al., “A Robust System for Longitudinal Knee Joint Edema and Blood Flow Assessment Based on Vector Bioimpedance Measurements,” IEEE Transactions on Biomedical Circuits and Systems, vol. 10, no. 3, pp. 545–555, Jun. 2016, conference Name: IEEE Transactions on Biomedical Circuits and Systems.
[4] R. C. Webb et al., “Epidermal devices for noninvasive, precise, and continuous mapping of macrovascular and microvascular blood flow,” Science Advances, vol. 1, no. 9, p. e1500701, Oct. 2015.
[5] M. A. Serhani et al., “ECG Monitoring Systems: Review, Architecture, Processes, and Key Challenges,” Sensors (Basel, Switzerland), vol. 20, no. 6, p. 1796, Mar. 2020.
[6] D. Castaneda et al., “A review on wearable photoplethysmography sensors and their potential future applications in health care,” International journal of biosensors & bioelectronics, vol. 4, no. 4, pp. 195–202, 2018.
[7] S. Hersek et al., “Wearable Vector Electrical Bioimpedance System to Assess Knee Joint Health,” IEEE Transactions on Biomedical Engineering, vol. 64, no. 10, pp. 2353–2360, Oct. 2017, conference Name: IEEE Transactions on Biomedical Engineering.
[8] R. Chaoshi et al., “Development of electrical bioimpedance technology in the future,” in Proceedings of the 20th Annual International Conference of the IEEE Engineering in Medicine and Biology Society. Vol.20 Biomedical Engineering Towards the Year 2000 and Beyond (Cat. No.98CH36286), vol. 2, 1998, pp. 1052–1054 vol.2.
[9] V. P. Rachim and W.-Y. Chung, “Multimodal Wrist Biosensor for Wearable Cuff-less Blood Pressure Monitoring System,” Scientific Reports, vol. 9, no. 1, p. 7947, May 2019, publisher: Nature Publishing Group.
[10] Y. Sattar and L. Chhabra, “Electrocardiogram,” in StatPearls. Treasure Island (FL): StatPearls Publishing, 2024.
[11] E. Trag¨ ardh ˚ et al., “How many ECG leads do we need?” Cardiology Clinics, vol. 24, no. 3, pp. 317–330, Aug. 2006.
[12] S. P. Preejith et al., “Wearable ECG platform for continuous cardiac monitoring,” in 2016 38th Annual International Conference of the IEEE Engineering in Medicine and Biology Society (EMBC), Aug. 2016, pp. 623–626, iSSN: 1558-4615.
[13] E. Richard and A. D. C. Chan, “Design of a gel-less two-electrode ECG monitor,” in 2010 IEEE International Workshop on Medical Measurements and Applications. Ottawa, ON, Canada: IEEE, Apr. 2010, pp. 92–96.
[14] A. R. Perez-Riera ´ | et al., “Main artifacts in electrocardiography,” Annals
of Noninvasive Electrocardiology : The Official Journal of the International Society for Holter and Noninvasive Electrocardiology, Inc, vol. 23, no. 2, p. e12494, Sep. 2017.
[15] N. V. Thakor and J. G. Webster, “Ground-Free ECG Recording with Two Electrodes,” IEEE Transactions on Biomedical Engineering, vol. BME-27, no. 12, pp. 699–704, Dec. 1980, conference Name: IEEE Transactions on Biomedical Engineering.
[16] T. Tamura, “Current progress of photoplethysmography and SPO2 for health monitoring,” Biomedical Engineering Letters, vol. 9, no. 1, pp. 21–36, Feb. 2019.
[17] S. Ghosh et al., “Continuous blood pressure prediction from pulse transit time using ECG and PPG signals,” in 2016 IEEE Healthcare Innovation Point-Of-Care Technologies Conference (HI-POCT), Nov. 2016, pp. 188–191.
[18] R. T. Tregear, “Interpretation of Skin Impedance Measurements,” Nature, vol. 205, no. 4971, pp. 600–601, Feb. 1965, publisher: Nature Publishing Group.
[19] S. Grimnes and G. Martinsen, “Chapter 10 - Selected Applications,” in Bioimpedance and Bioelectricity Basics (Third Edition), S. Grimnes and
G. Martinsen, Eds. Oxford: Academic Press, Jan. 2015, pp. 405–494.
[20] D. Bouchaala et al., “High accurate and wideband current excitation for bioimpedance health monitoring systems,” Measurement, vol. 79, pp. 339–348, Feb. 2016.
[21] H. Toreyin ¨ et al., “Proof-of-concept energy-efficient and real-time hemodynamic feature extraction from bioimpedance signals using a mixedsignal field programmable analog array.” IEEE, 2017, pp. 233–236.

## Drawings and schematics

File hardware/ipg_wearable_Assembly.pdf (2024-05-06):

# IPG Wearable V1.0

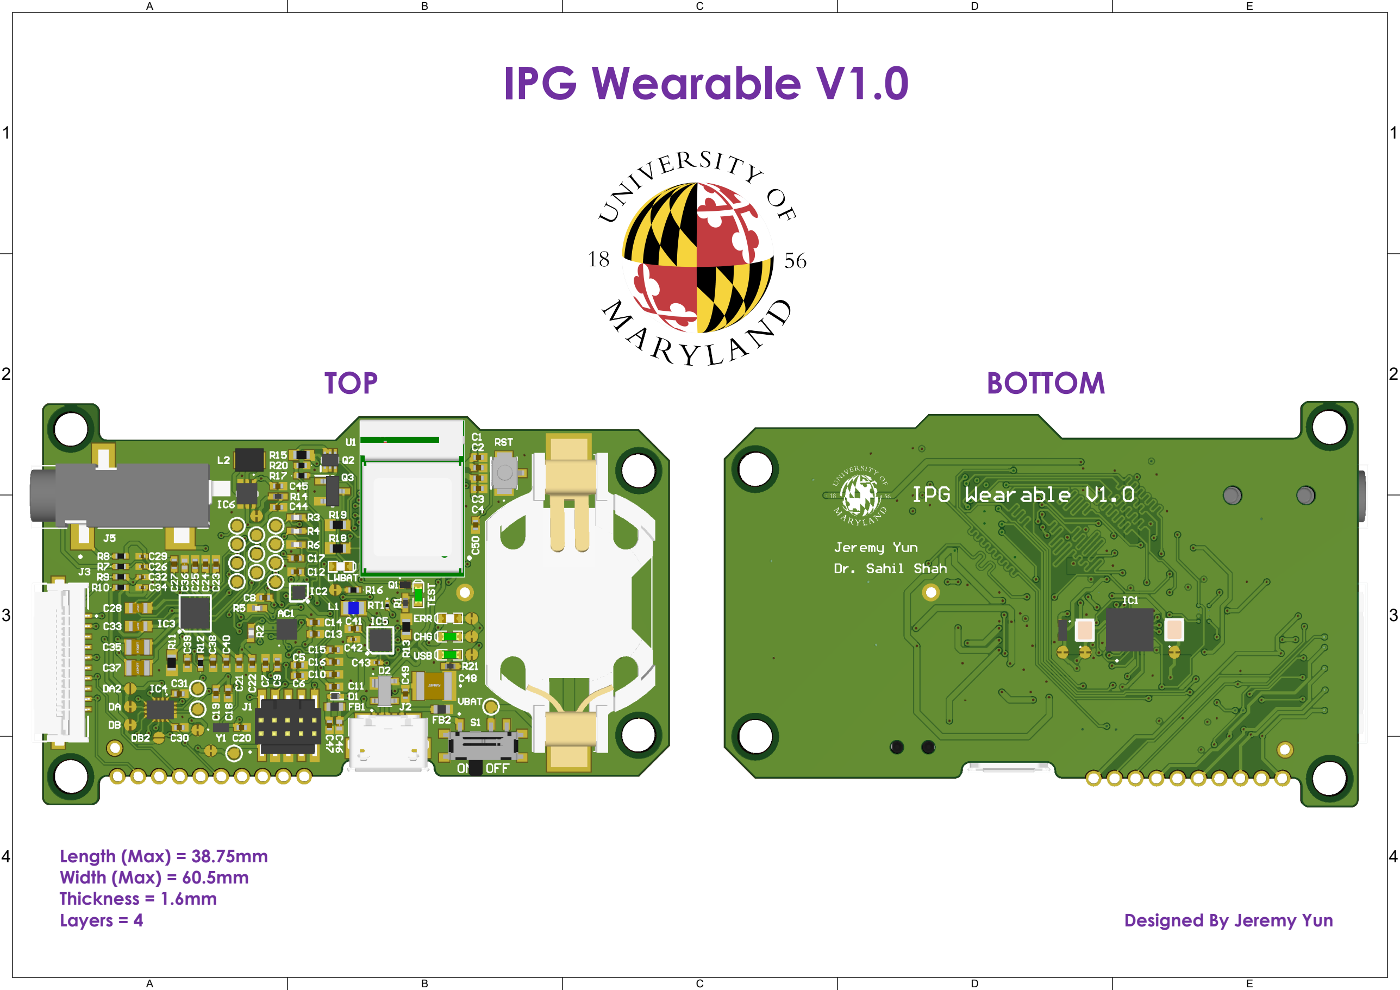
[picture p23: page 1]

A

B

C

D

E

1 | 1
2 | 2
3 | 3
4 | 4
TOP | BOTTOM

### Designed By Jeremy Yun

### Length (Max) = 38.75mm Width (Max) = 60.5mm Thickness = 1.6mm Layers = 4

# BOTTOM

# IPG Wearable V1.0 - Isometric Views

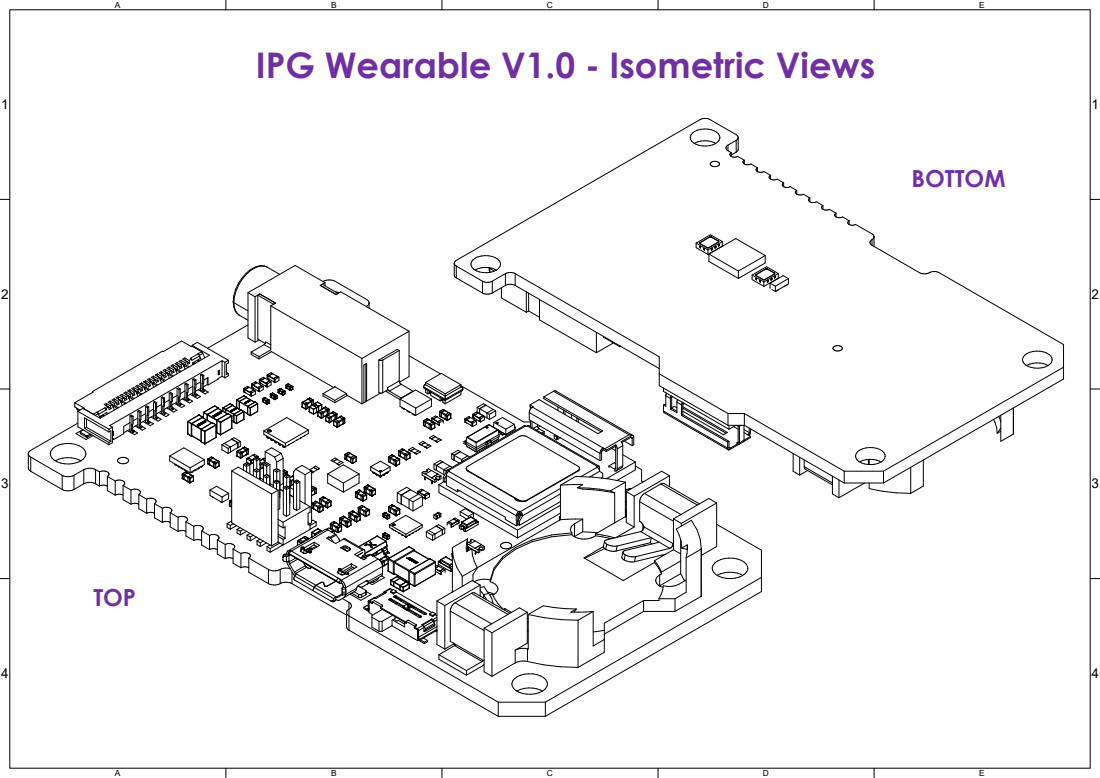
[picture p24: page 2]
TOP

# IPG Wearable V1.0 - Assembly Top

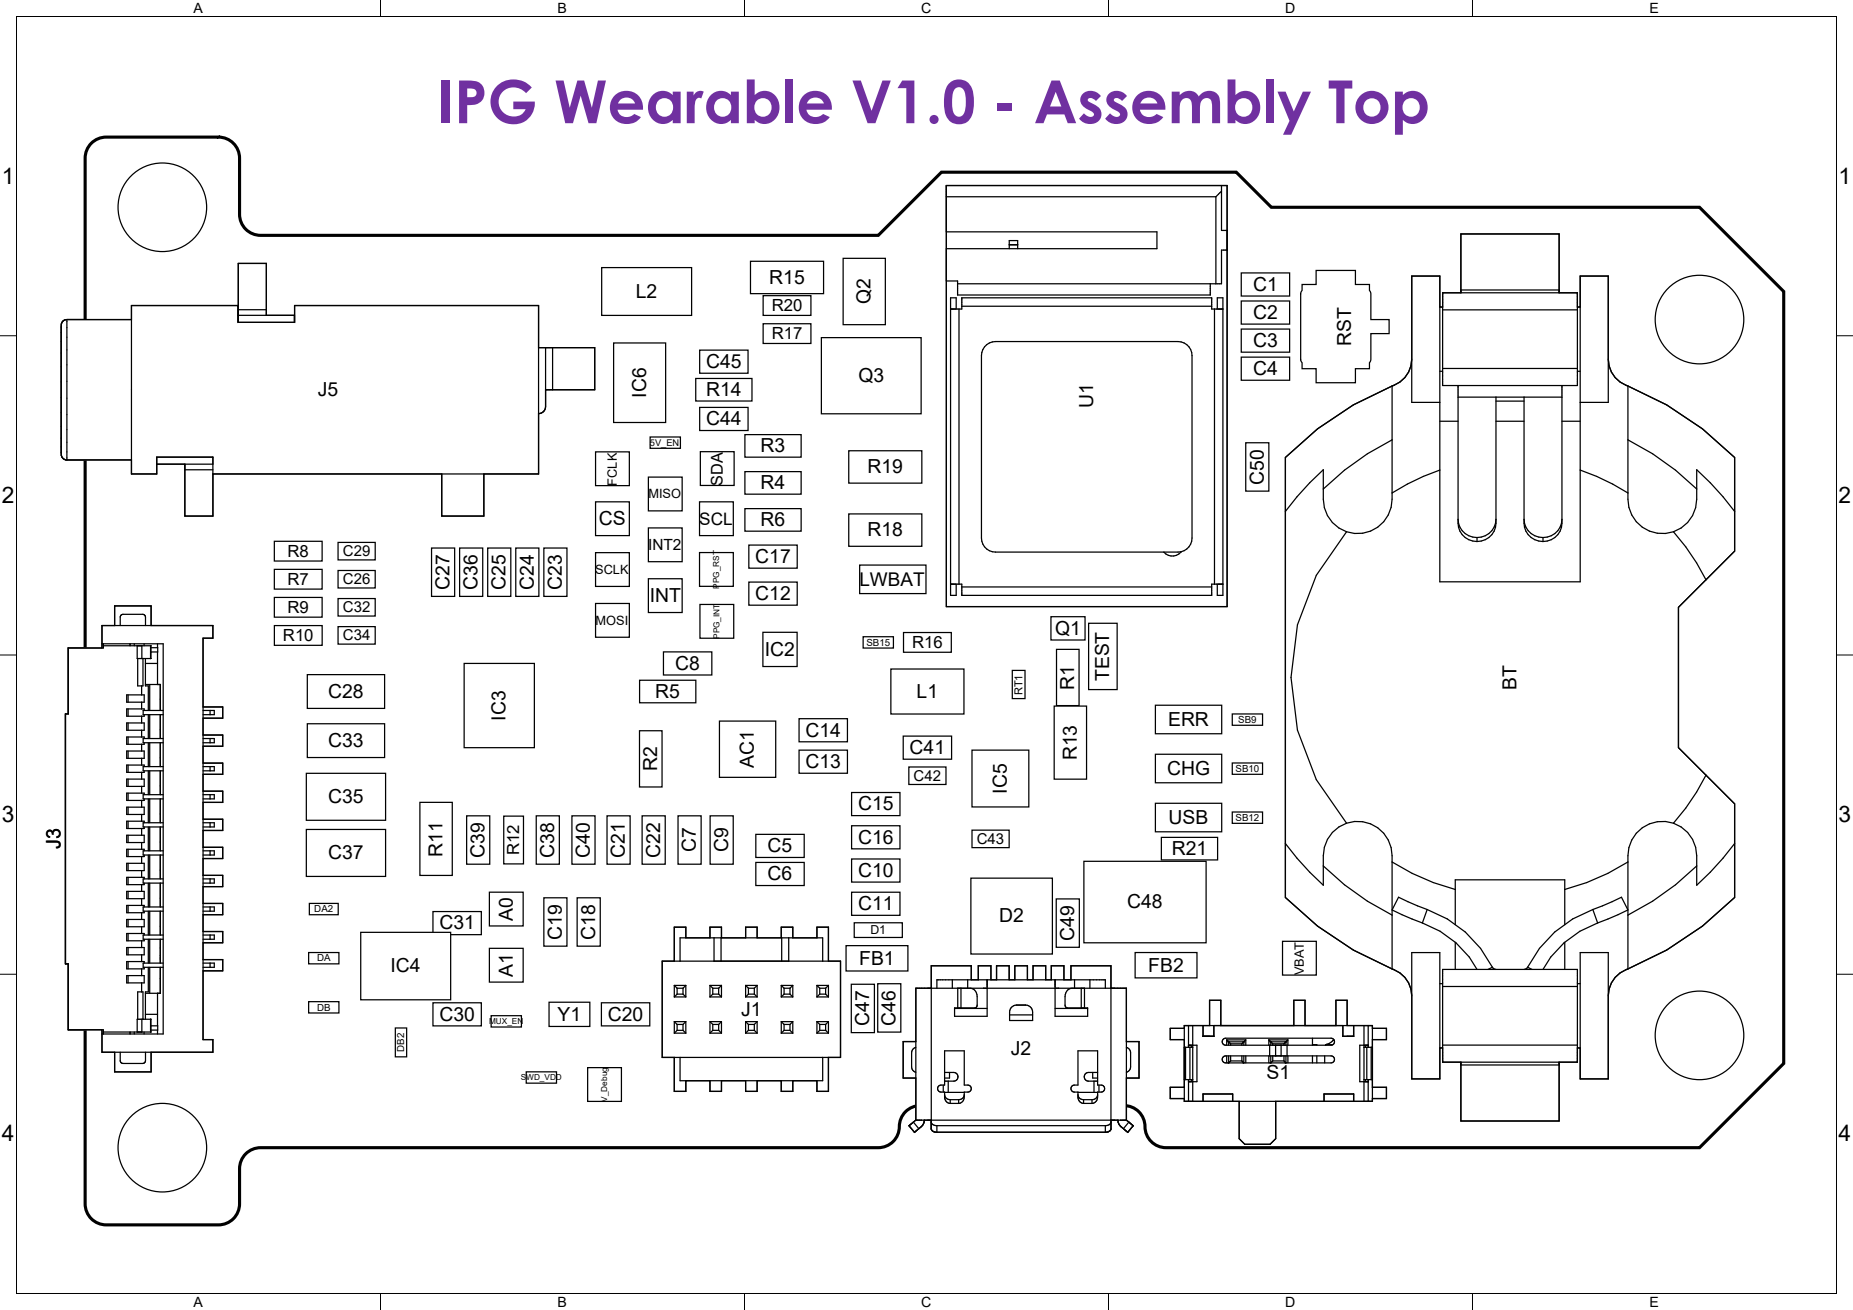
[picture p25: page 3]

# IPG Wearable V1.0 - Assembly Bottom

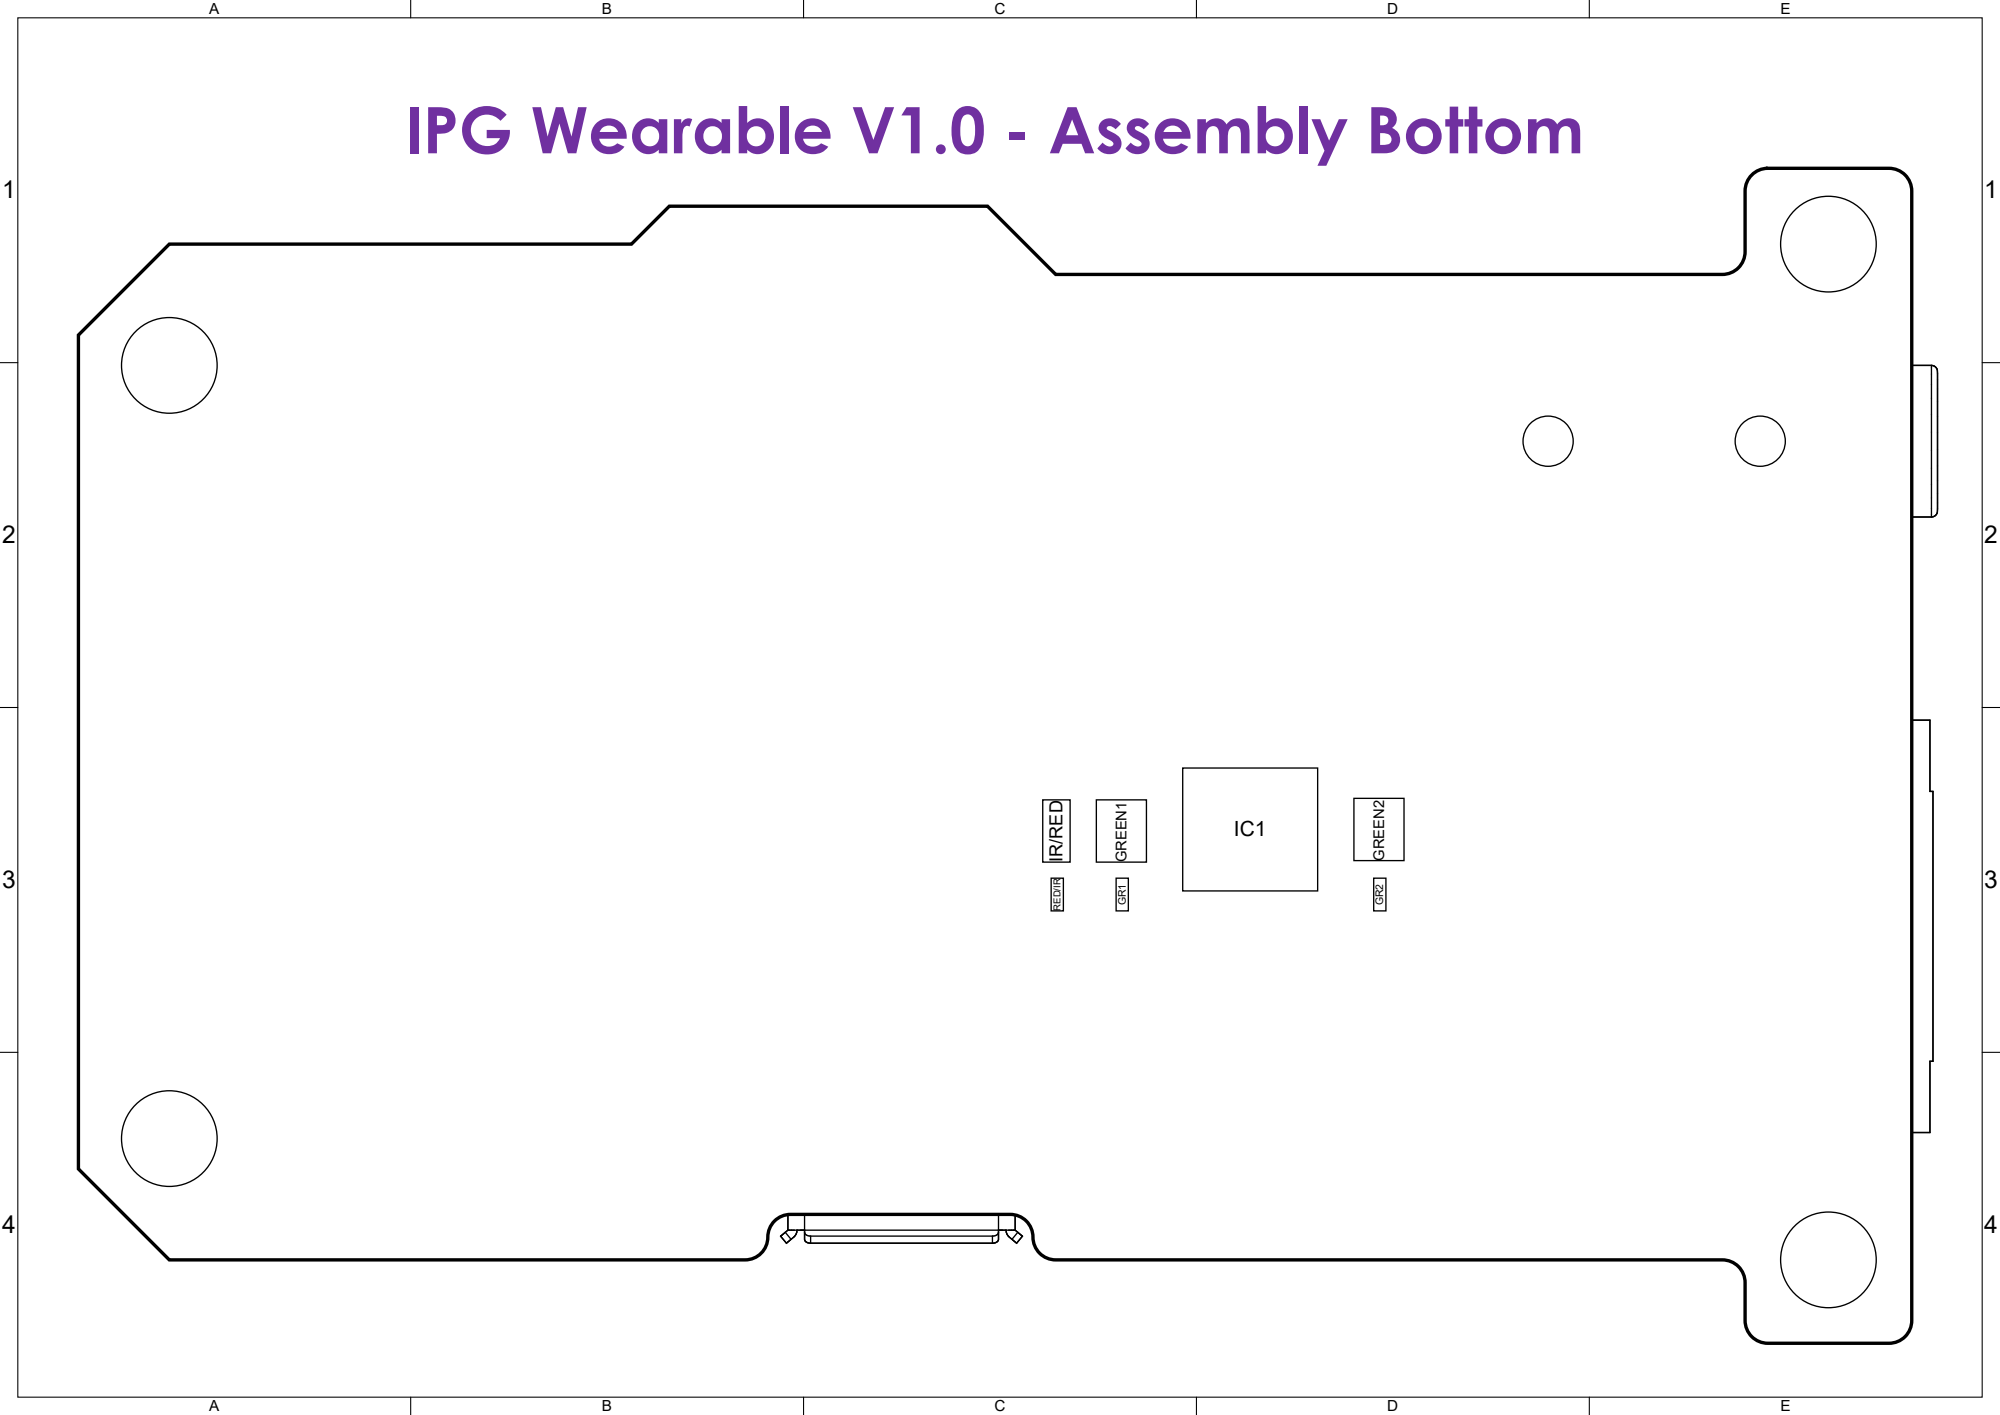
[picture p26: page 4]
4 GR¹; GR² RED/IR IR/RED; GREEN¹; GREEN²

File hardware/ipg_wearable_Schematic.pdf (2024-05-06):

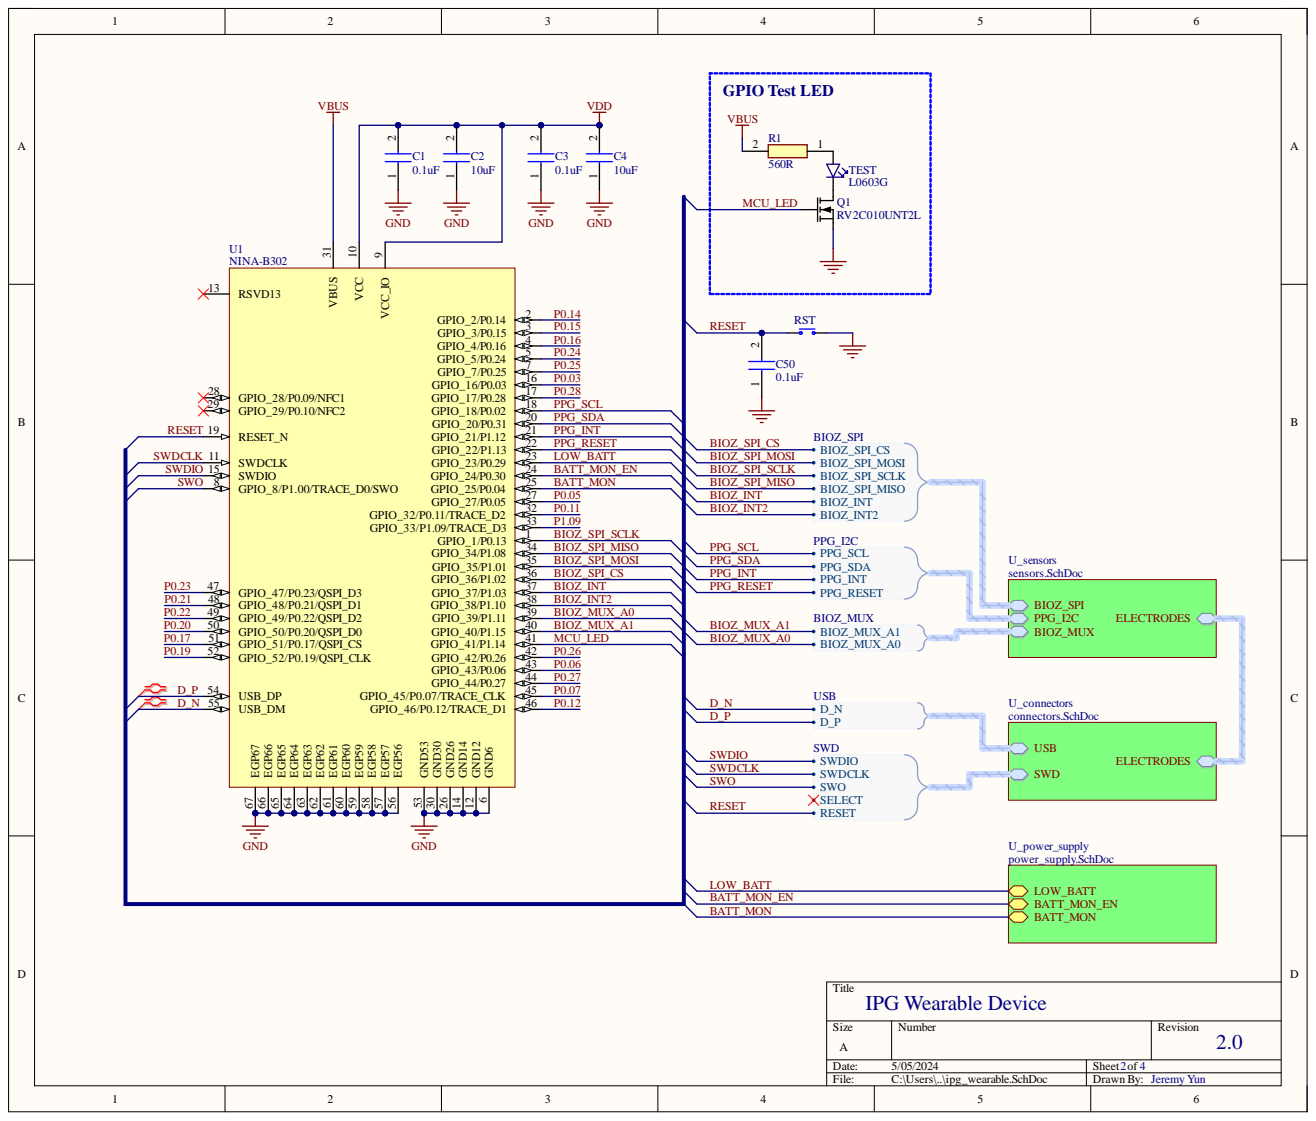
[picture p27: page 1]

U 1 NIN A -B 3 0 2 | | G N D

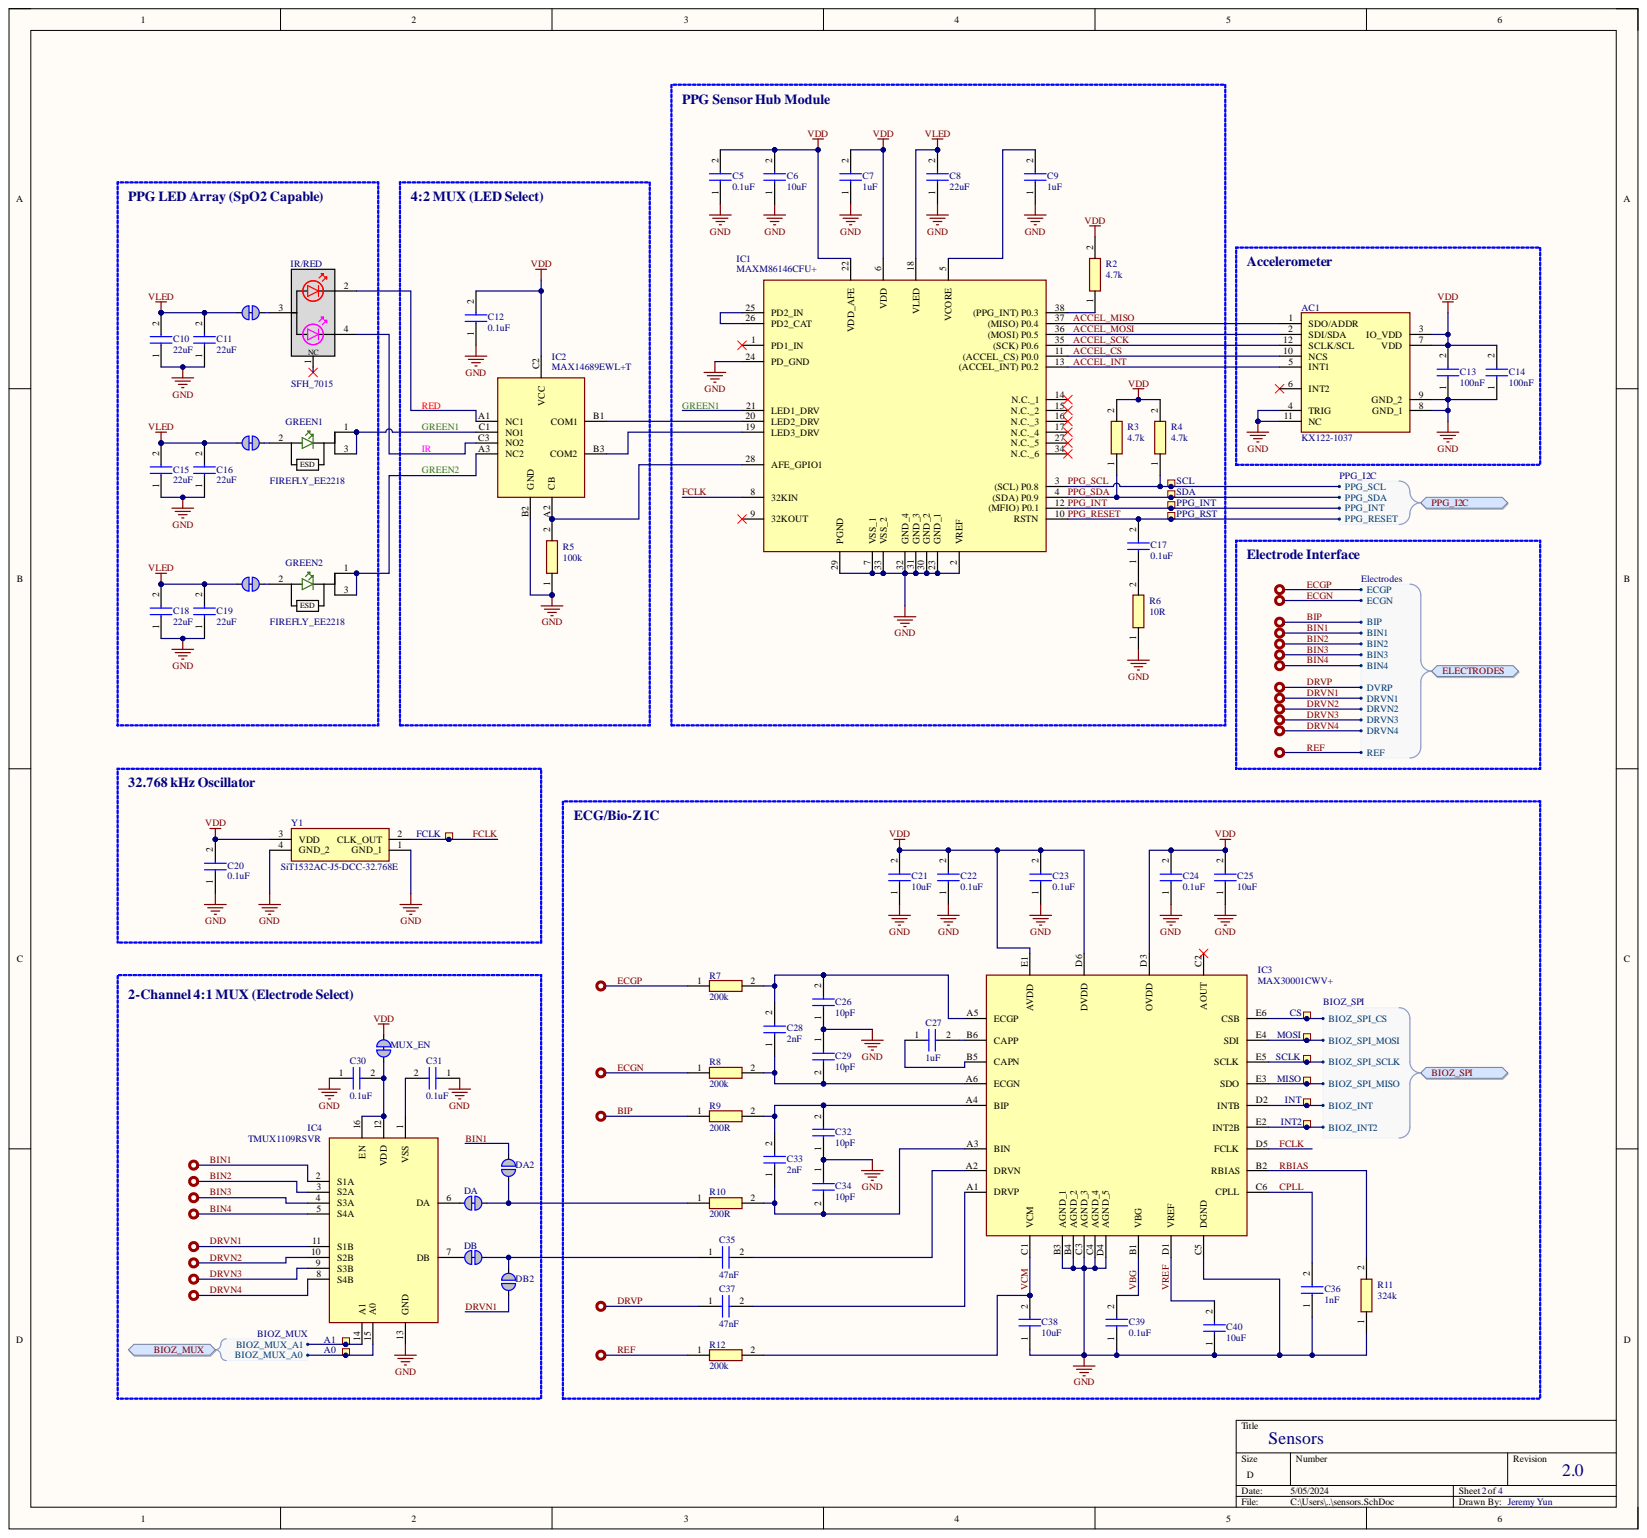
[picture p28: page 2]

PPG Sensor Hub Module

PD1_IN 1 | ACCEL_MOSI

2-Channel 4:1 MUX (Electrode Select)

BIN A3

DRVN A2 | RBIAS

BIN3 | S2A 3

C34 GND | | DRVP A1 | CPLL

DRVN3
DRVN4

Size D | Number | Revision

Date: 5/05/2024 | Sheet of
File: C:\Users\..\sensors.SchDoc | Drawn By: Jeremy Yun

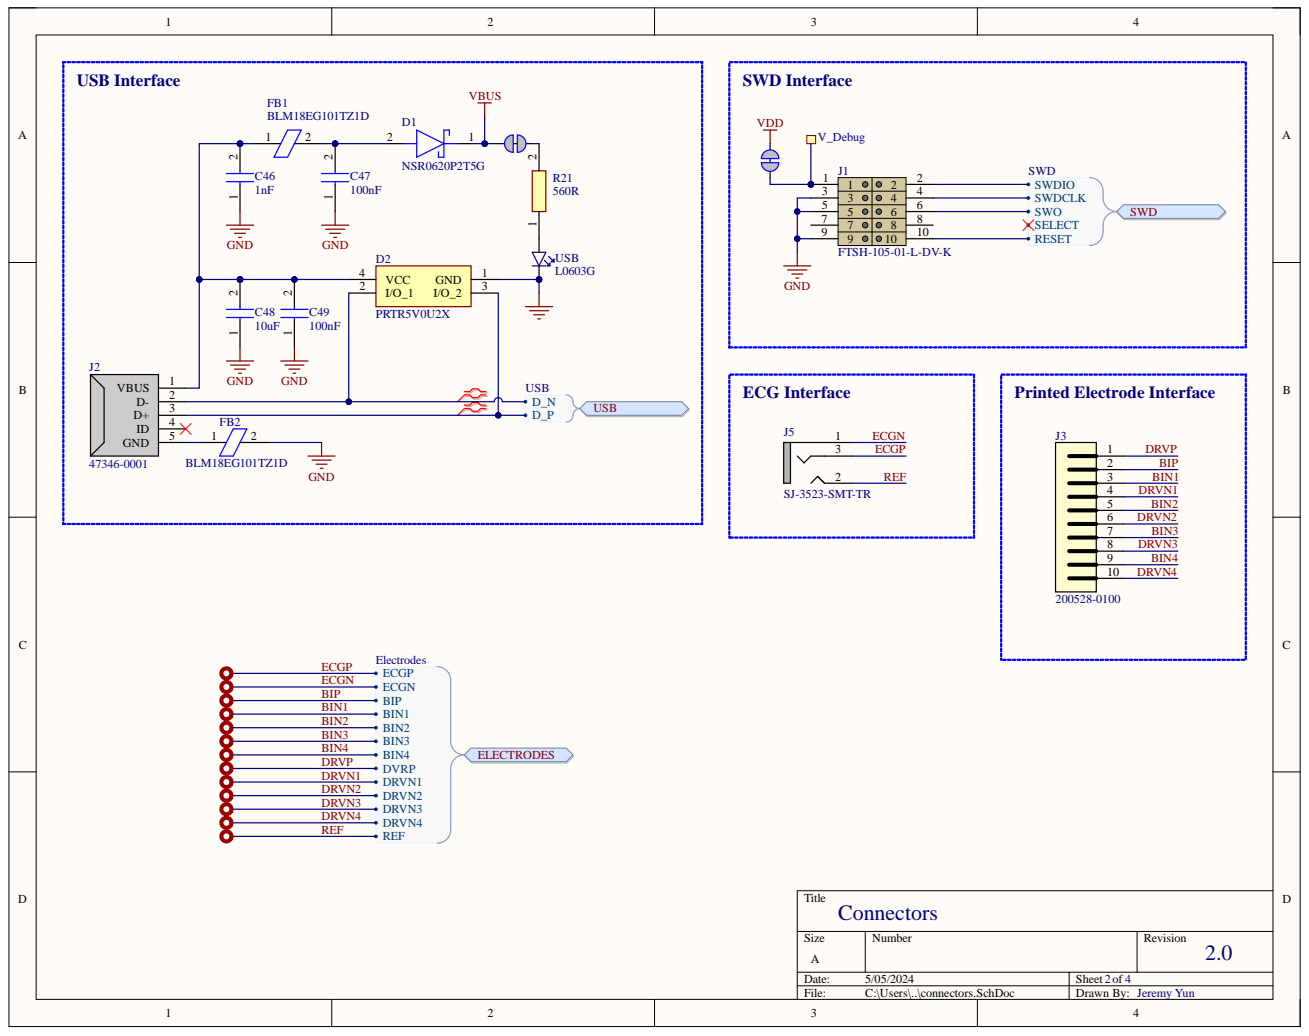
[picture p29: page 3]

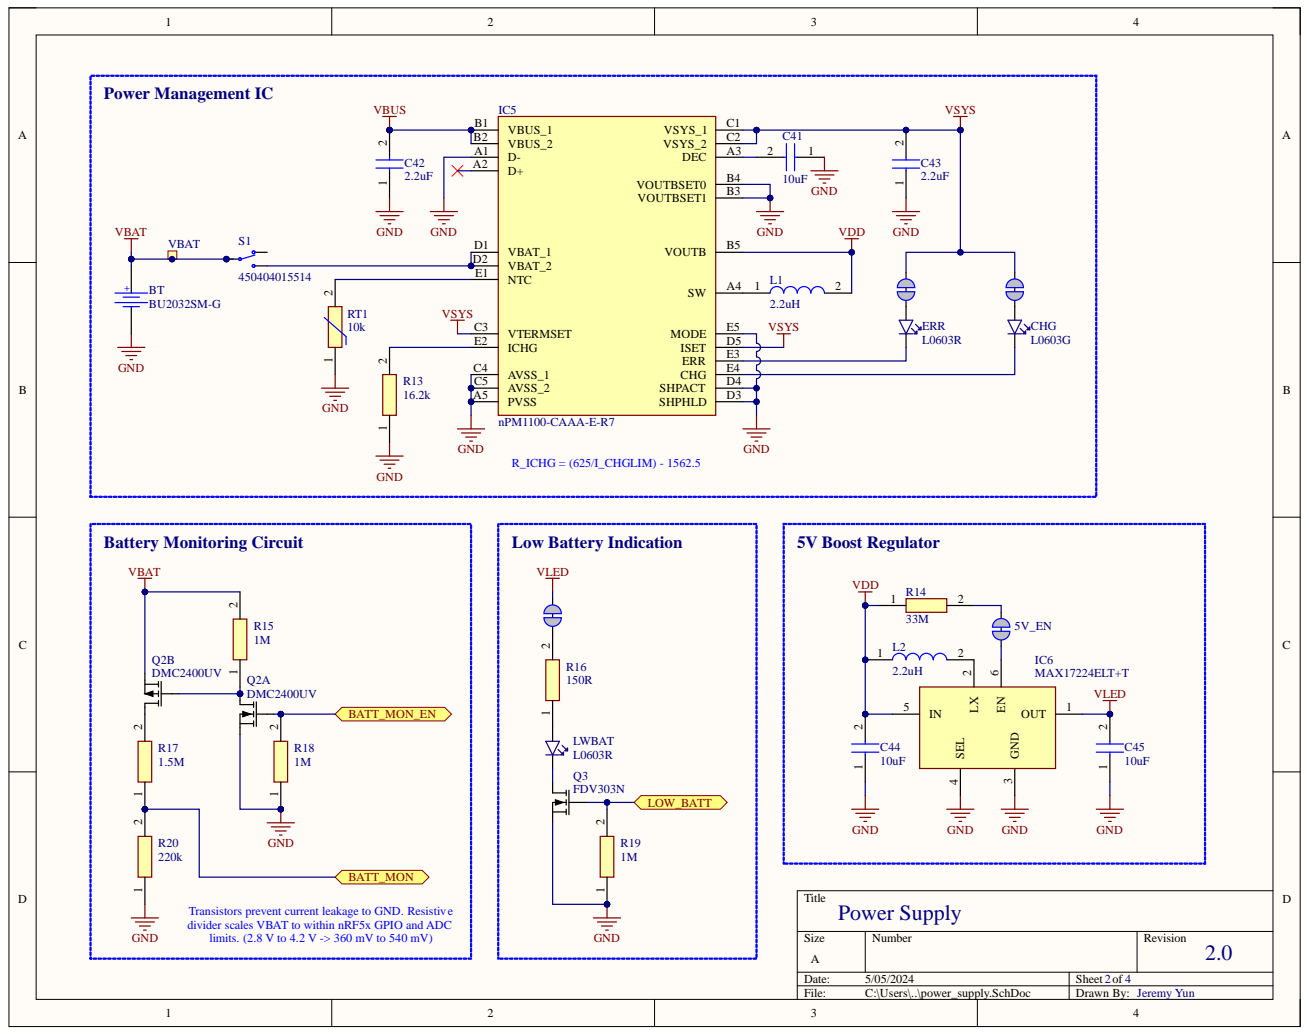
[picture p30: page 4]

Transistors prevent current leakage to GND. Resistive
divider scales VBAT to within nRF5x GPIO and ADC
limits. (2.8 V to 4.2 V -> 360 mV to 540 mV)

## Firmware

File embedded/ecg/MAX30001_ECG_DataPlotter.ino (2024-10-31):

//////////////////////////////////////////////////////////////////////////////////////////
//
//  Header for the MAX30001
//
//  This software is licensed under the MIT License(http://opensource.org/licenses/MIT).
//
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
//
/////////////////////////////////////////////////////////////////////////////////////////

#include <Arduino.h>
#include <SPI.h>

#define WREG 0x00
#define RREG 0x01

#define   NO_OP           0x00
#define   STATUS          0x01
#define   EN_INT          0x02
#define   EN_INT2         0x03
#define   MNGR_INT        0x04
#define   MNGR_DYN        0x05
#define   SW_RST          0x08
#define   SYNCH           0x09
#define   FIFO_RST        0x0A
#define   INFO            0x0F
#define   CNFG_GEN        0x10
#define   CNFG_CAL        0x12
#define   CNFG_EMUX       0x14
#define   CNFG_ECG        0x15
#define   CNFG_BMUX       0x17
#define   CNFG_BIOZ       0x18
#define   CNFG_PACE       0x1A
#define   CNFG_RTOR1      0x1D
#define   CNFG_RTOR2      0x1E
#define   ECG_FIFO_BURST  0x20
#define   ECG_FIFO        0x21
#define   BIOZ_FIFO_BURST 0x22
#define   BIOZ_FIFO       0x23
#define   RTOR            0x25
#define   PACE0_BURST     0x30
#define   PACE0_A         0x31
#define   PACE0_B         0x32
#define   PACE0_C         0x33
#define   PACE1_BURST     0x34
#define   PACE1_A         0x35
#define   PACE1_B         0x36
#define   PACE1_C         0x37
#define   PACE2_BURST     0x38
#define   PACE2_A         0x39
#define   PACE2_B         0x3A
#define   PACE2_C         0x3B
#define   PACE3_BURST     0x3C
#define   PACE3_A         0x3D
#define   PACE3_B         0x3E
#define   PACE3_C         0x3F
#define   PACE4_BURST     0x40
#define   PACE4_A         0x41
#define   PACE4_B         0x42
#define   PACE4_C         0x43
#define   PACE5_BURST     0x44
#define   PACE5_A         0x45
#define   PACE5_B         0x46
#define   PACE5_C         0x47
#define   NO_OP           0x7F

#define MAX30001_CS_PIN   10
#define CLK_PIN           6
#define RTOR_INTR_MASK    0x04

typedef enum
{
  SAMPLINGRATE_128 = 128, 
  SAMPLINGRATE_256 = 256, 
  SAMPLINGRATE_512 = 512
} sampRate;



typedef struct
{
    signed long value;
    uint8_t e_tag;
    uint8_t p_tag;
} ecg_data;

typedef struct
{
    signed long value;
    uint8_t b_tag;
} bioz_data;

class MAX30001
{
  public:
  	unsigned int heartRate;
  	unsigned int RRinterval;
    ecg_data ecgData;
    bioz_data biozData;

    void max30001Begin();
    void max30001BeginRtoRMode();
    void max30001SwReset(void);
    void getHRandRR(void);
    void getEcgSample(void);
    void getBioZSample(void);
    bool max30001ReadInfo(void);
    void max30001SetSamplingRate(uint16_t samplingRate);
    void max30001RegRead(uint8_t Reg_address, uint8_t * buff);
    void max30001RegWrite (unsigned char WRITE_ADDRESS, unsigned long data);
    uint8_t max30001GetEcgGain(void);
    uint8_t max30001GetBioZGain(void);

  private:
    void max30001ReadData(int num_samples, uint8_t * readBuffer);
    void max30001Synch(void);
    void max30001FIFO_Rst(void);
};


/*-------------------------------------------------------------------------------------------------------------*/


//////////////////////////////////////////////////////////////////////////////////////////
//
//  Library code for the MAX30001
//
//  Arduino connections:
//
//  |MAX30001 pin label| Pin Function         |Arduino Connection|
//  |----------------- |:--------------------:|-----------------:|
//  | POCI             | Peripheral Out       |  D12             |
//  | PICO             | Peripheral In        |  D11             |
//  | SCLK             | Serial Clock         |  D13             |
//  | CS               | Chip Select          |  D10             |
//  | VCC              | Digital VDD          |  +5V             |
//  | GND              | Digital Gnd          |  Gnd             |
//  | FCLK             | 32K CLOCK            |  -               |
//  | INT1             | Interrupt1           |  D01             |
//  | INT2             | Interrupt2           |  -               |
//
//  This software is licensed under the MIT License(http://opensource.org/licenses/MIT).
//
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
NG FROM, OUT OF OR IN CONNECTION WITH THE
//  SOFTWARE OR THE USE OR OTHER DEALINGS IN THE SOFTWARE.
//
//
/////////////////////////////////////////////////////////////////////////////////////////

void MAX30001::max30001RegWrite(unsigned char WRITE_ADDRESS, unsigned long data)
{
    // now combine the register address and the command into one byte:
    byte dataToSend = (WRITE_ADDRESS << 1) | WREG;

     // take the chip select low to select the device:
    digitalWrite(MAX30001_CS_PIN, LOW);

    delay(2);
    SPI.transfer(dataToSend);
    SPI.transfer(data >> 16);
    SPI.transfer(data >> 8);
    SPI.transfer(data);
    delay(2);

    // take the chip select high to de-select:
    digitalWrite(MAX30001_CS_PIN, HIGH);
}


void MAX30001::max30001SwReset(void)
{
    max30001RegWrite(SW_RST, 0x000000);
    delay(100);
}

void MAX30001::max30001Synch(void)
{
    max30001RegWrite(SYNCH, 0x000000);
}

void MAX30001::max30001FIFO_Rst(void) {
    max30001RegWrite(FIFO_RST, 0x000000);
}

void MAX30001::max30001RegRead(uint8_t Reg_address, uint8_t * buff)
{
    uint8_t spiTxBuff;

    digitalWrite(MAX30001_CS_PIN, LOW);

    spiTxBuff = (Reg_address << 1 ) | RREG;
    SPI.transfer(spiTxBuff);              // Send register location

    for ( int i = 0; i < 3; i++)
    {
       buff[i] = SPI.transfer(0xFF);
    }

    digitalWrite(MAX30001_CS_PIN, HIGH);
}

bool MAX30001::max30001ReadInfo(void)
{
    uint8_t spiTxBuff;
    uint8_t readBuff[4] ;

    digitalWrite(MAX30001_CS_PIN, LOW);

    spiTxBuff = (INFO << 1 ) | RREG;
    SPI.transfer(spiTxBuff);              // Send register location

    for ( int i = 0; i < 3; i++)
    {
       readBuff[i] = SPI.transfer(0xFF);
    }

    digitalWrite(MAX30001_CS_PIN, HIGH);

    if((readBuff[0] & 0xF0) == 0x50 ){

      Serial.println("Max30001 is ready.");
      Serial.print("Rev ID:  ");
      Serial.println((readBuff[0] & 0xF0));

      return true;
    }else{
      Serial.println("Max30001 read info error.\n");
      return false;
    }

    return false;
}

void MAX30001::max30001ReadData(int num_samples, uint8_t * readBuffer)
{
    uint8_t spiTxBuff;
    digitalWrite(MAX30001_CS_PIN, LOW);

    spiTxBuff = (ECG_FIFO_BURST << 1 ) | RREG;
    SPI.transfer(spiTxBuff);                  // Send register location

    for ( int i = 0; i < num_samples*3; ++i)
    {
      readBuffer[i] = SPI.transfer(0x00);
    }

    digitalWrite(MAX30001_CS_PIN, HIGH);
}

void MAX30001::max30001Begin()
{
    max30001SwReset();
    delay(100);
    max30001RegWrite(CNFG_GEN, 0x081007);
    delay(100);
    max30001RegWrite(CNFG_CAL, 0x720000);
    delay(100);
    max30001RegWrite(CNFG_EMUX,0x0B0000);
    delay(100);
    max30001RegWrite(CNFG_ECG, 0x805000);     // d23 - d22 : 10 for 250sps , 00:500 sps
    delay(100);

    max30001RegWrite(CNFG_RTOR1, 0x3FC600);
    max30001Synch();
    delay(100);
}

void MAX30001::max30001BeginRtoRMode()
{
    max30001SwReset();
    delay(100);
    max30001RegWrite(CNFG_GEN, 0x080004);
    delay(100);
    max30001RegWrite(CNFG_CAL, 0x720000);   // 0x700000
    delay(100);
    max30001RegWrite(CNFG_EMUX,0x0B0000);
    delay(100);
    max30001RegWrite(CNFG_ECG, 0x805000);   // d23 - d22 : 10 for 250sps , 00:500 sps
    delay(100);
    max30001RegWrite(CNFG_RTOR1, 0x3FC600);
    delay(100);
    max30001RegWrite(EN_INT, 0x000401);
    delay(100);
    max30001Synch();
    delay(100);
}

//not tested
void MAX30001::max30001SetSamplingRate(uint16_t samplingRate)
{
    uint8_t regBuff[4] = {0};
    max30001RegRead(CNFG_ECG, regBuff);

    switch(samplingRate){
        case SAMPLINGRATE_128:
                regBuff[0] = (regBuff[0] | 0x80 );
            break;

        case SAMPLINGRATE_256:
                regBuff[0] = (regBuff[0] | 0x40 );
            break;

        case SAMPLINGRATE_512:
                regBuff[0] = (regBuff[0] | 0x00 );
            break;

        default :
            Serial.println("Invalid sampling rate, please choose between {128, 256, 512}.");
            break;
    }

    unsigned long cnfgEcg;
    memcpy(&cnfgEcg, regBuff, 4);

    Serial.print("cnfg ECG ");
    Serial.println((cnfgEcg));
    max30001RegWrite(CNFG_ECG, (cnfgEcg >> 8));
}

uint8_t MAX30001::max30001GetEcgGain(void)
{
    uint8_t regReadBuff[4];
    uint8_t ecg_gains[] = {20, 40, 80, 160};
    // uint8_t ecg_gains[4];
    // ecg_gains[0] = 20;
    // ecg_gains[1] = 40;
    // ecg_gains[2] = 80;
    // ecg_gains[3] = 160;
    uint8_t gain_idx = 0;

    max30001RegRead(CNFG_ECG, regReadBuff);
    gain_idx = regReadBuff[0] & 0x03;

    return ecg_gains[gain_idx];
}

uint8_t MAX30001::max30001GetBioZGain(void)
{
    uint8_t regReadBuff[4];
    uint8_t bioz_gains[] = {10, 20, 40, 80};
    uint8_t gain_idx = 0;

    max30001RegRead(CNFG_BIOZ, regReadBuff);
    gain_idx = regReadBuff[0] & 0x03;

    return bioz_gains[gain_idx];
}

void MAX30001::getHRandRR(void)
{
    uint8_t regReadBuff[4];
    max30001RegRead(RTOR, regReadBuff);

    unsigned long RTOR_msb = (unsigned long) (regReadBuff[0]);
    unsigned char RTOR_lsb = (unsigned char) (regReadBuff[1]);
    unsigned long rtor = (RTOR_msb << 8 | RTOR_lsb);
    rtor = ((rtor >> 2) & 0x3FFF) ;

    float hr =  60 /((float)rtor*0.0078125);
    heartRate = (unsigned int)hr;

    unsigned int RR = (unsigned int)rtor* (7.8125) ;  //8ms
    RRinterval = RR;
}

void MAX30001::getEcgSample(void)
{
    signed long ecg_reading;
    uint8_t regReadBuff[4];
    max30001RegRead(ECG_FIFO, regReadBuff);

    unsigned long data0 = (unsigned long) (regReadBuff[0]);
    data0 = data0 << 16;
    unsigned long data1 = (unsigned long) (regReadBuff[1]);
    data1 = data1 << 8;
    unsigned long data2 = (unsigned long) (regReadBuff[2]);
    data2 = data2 & 0xC0;                                   // Extract ECG_FIFO[7:6]
    unsigned long data = (unsigned long) (data0 | data1 | data2);
    ecgData.value = (signed long) ( data >> 6);             // ECG ADC data is ECG_FIFO[23:6]

    ecgData.e_tag = (regReadBuff[2] & 0x38) >> 3;           // Align ETAG[2:0] to 8-bit val. 0b00XXX000 -> 0b00000XXX
    ecgData.p_tag = regReadBuff[2] & 0x07;                  // PTAG[2:0] is already aligned. 0b00000XXX

    if(ecgData.e_tag & 0x7){                                // FIFO Overflow Exception: ETAG[2:0] = 111, send RST
        max30001FIFO_Rst();
    }
}

void MAX30001::getBioZSample(void)
{
    uint8_t regReadBuff[4];
    max30001RegRead(BIOZ_FIFO, regReadBuff);

    unsigned long data0 = (unsigned long) (regReadBuff[0]);
    data0 = data0 << 16;
    unsigned long data1 = (unsigned long) (regReadBuff[1]);
    data1 = data1 << 8;
    unsigned long data2 = (unsigned long) (regReadBuff[2]);
    data2 = data2 & 0xF0;                                   // Extract BIOZ_FIFO[7:4]
    unsigned long data = (unsigned long) (data0 | data1 | data2);
    biozData.value = (signed long) (data >> 4);             // BioZ ADC data is BIOZ_FIFO[23:4]

    biozData.b_tag = regReadBuff[2] & 0x07;                 // BTAG[2:0] is BIOZ_FIFO[2:0]
}






/*-------------------------------------------------------------------------------------------------------------*/
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

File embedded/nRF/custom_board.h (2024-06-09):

/**
 * Copyright (c) 2016 - 2020, Nordic Semiconductor ASA
 *
 * All rights reserved.
 *
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
 * 3. Neither the name of Nordic Semiconductor ASA nor the names of its
 *    contributors may be used to endorse or promote products derived from this
 *    software without specific prior written permission.
 *
 * 4. This software, with or without modification, must only be used with a
 *    Nordic Semiconductor ASA integrated circuit.
 *
 * 5. Any software provided in binary form under this license must not be reverse
 *    engineered, decompiled, modified and/or disassembled.
 *
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
 */

/**
 Modified by u-blox 2020
*/

#ifndef CUSTOM_BOARD_H
#define CUSTOM_BOARD_H

#ifdef __cplusplus
extern "C" {
#endif

#include "nrf_gpio.h"

// In this file PIN 25 is used as button SWITCH_1, if the GREEN led
// should be used it is possible to defined that one instead.
#define LEDS_NUMBER    2

#define LED_1          NRF_GPIO_PIN_MAP(0,13)	// RED
#define LED_2          NRF_GPIO_PIN_MAP(1,00)	// BLUE
// #define LED_3       NRF_GPIO_PIN_MAP(0,25)	// GREEN

#define LEDS_ACTIVE_STATE 0

#define LEDS_LIST { LED_1, LED_2 }

#define LEDS_INV_MASK  LEDS_MASK

#define BSP_LED_0      LED_1
#define BSP_LED_1      LED_2
// #define BSP_LED_2   LED_3

#define BUTTONS_NUMBER 2

#define BUTTON_1       25  // SWITCH_1	
#define BUTTON_2       2   // SWITCH_2
#define BUTTON_PULL    NRF_GPIO_PIN_PULLUP

#define BUTTONS_ACTIVE_STATE 0

#define BUTTONS_LIST { BUTTON_1, BUTTON_2 }

#define BSP_BUTTON_0   BUTTON_1
#define BSP_BUTTON_1   BUTTON_2

#define RX_PIN_NUMBER  NRF_GPIO_PIN_MAP(0,29)
#define TX_PIN_NUMBER  NRF_GPIO_PIN_MAP(1,13)
#define CTS_PIN_NUMBER NRF_GPIO_PIN_MAP(1,12)
#define RTS_PIN_NUMBER NRF_GPIO_PIN_MAP(0,31)
#define HWFC           true

#define BSP_QSPI_SCK_PIN   19
#define BSP_QSPI_CSN_PIN   17
#define BSP_QSPI_IO0_PIN   20
#define BSP_QSPI_IO1_PIN   21
#define BSP_QSPI_IO2_PIN   22
#define BSP_QSPI_IO3_PIN   23

// Arduino board mappings
#define ARDUINO_SCL_PIN             24  // SCL signal pin
#define ARDUINO_SDA_PIN             16  // SDA signal pin

#define ARDUINO_13_PIN              NRF_GPIO_PIN_MAP(0, 7)
#define ARDUINO_12_PIN              NRF_GPIO_PIN_MAP(0, 2)
#define ARDUINO_11_PIN              NRF_GPIO_PIN_MAP(0, 15)
#define ARDUINO_10_PIN              NRF_GPIO_PIN_MAP(0, 14)
#define ARDUINO_9_PIN               NRF_GPIO_PIN_MAP(0, 12)
#define ARDUINO_8_PIN               NRF_GPIO_PIN_MAP(1, 9)

#define ARDUINO_7_PIN               NRF_GPIO_PIN_MAP(0, 10)
#define ARDUINO_6_PIN               NRF_GPIO_PIN_MAP(0, 9)
#define ARDUINO_5_PIN               NRF_GPIO_PIN_MAP(0, 11)
#define ARDUINO_4_PIN               NRF_GPIO_PIN_MAP(0, 13)
#define ARDUINO_3_PIN               NRF_GPIO_PIN_MAP(0, 31)
#define ARDUINO_2_PIN               NRF_GPIO_PIN_MAP(1, 12)
#define ARDUINO_1_PIN               NRF_GPIO_PIN_MAP(1, 13)
#define ARDUINO_0_PIN               NRF_GPIO_PIN_MAP(0, 29)
#define ARDUINO_A0_PIN              NRF_GPIO_PIN_MAP(0, 4)
#define ARDUINO_A1_PIN              NRF_GPIO_PIN_MAP(0, 30)
#define ARDUINO_A2_PIN              NRF_GPIO_PIN_MAP(0, 5)
#define ARDUINO_A3_PIN              NRF_GPIO_PIN_MAP(0, 2)
#define ARDUINO_A4_PIN              NRF_GPIO_PIN_MAP(0, 28)
#define ARDUINO_A5_PIN              NRF_GPIO_PIN_MAP(0, 3)
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

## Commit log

2024-02-26 Added prototype v1 ECG board
    [ecg_circuit.PrjPcb, ecg_circuit.csv, nrf52810_qcaa.DRL, nrf52810_qcaa.GBL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]
2024-02-26 edited v1-ecg-archive
    [ecg_circuit.PrjPcb, ecg_circuit.csv, nrf52810_qcaa.DRL, nrf52810_qcaa.GBL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]
2024-02-26 Add new v1 ecg archive
    [ecg_circuit.PrjPcb, ecg_circuit.csv, nrf52810_qcaa.DRL, nrf52810_qcaa.GBL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]
2024-02-26 added v2_ecg
    [ECG_board.SchLib, ecg_circuit.SchDoc, v1_ECG_board.PrjPcb]
2024-02-26 replace v2 sch
    [ecg_circuit.SchDoc]
2024-02-26 added ecg filter dir readme
2024-02-26 add ecg matlab filters
2024-03-06 changed name of filters folder
2024-03-06 add template for embedded arduino filter
2024-04-16 updated repo structure
    [ECG_board.SchLib, ecg_circuit.PrjPcb, ecg_circuit.SchDoc, ecg_circuit.csv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]
2024-05-06 adding altium files
    [V2_wearable.PcbLib, V2_wearable.PrjPcb, V2_wearable.SCHLIB, connectors.SchDoc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]
2024-05-06 changed hardware dir name
    [ECG_board.SchLib, V2_wearable.PcbLib, V2_wearable.PrjPcb, V2_wearable.SCHLIB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]
2024-06-09 deleted old files
    [ECG_board.SchLib, ecg_circuit.PrjPcb, ecg_circuit.SchDoc, ecg_circuit.csv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]
2024-06-09 changed dir
    [V2_wearable.PcbLib, V2_wearable.PrjPcb, V2_wearable.SCHLIB, connectors.SchDoc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]
2024-06-10 add electrode array design files
    [elec_array.PcbDoc, elec_array.PcbLib, elec_array.SchDoc, elec_array.SchLib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]
2024-08-24 Update README.md with fabricated board pictures
2024-10-31 adding ecg data plotter sample
